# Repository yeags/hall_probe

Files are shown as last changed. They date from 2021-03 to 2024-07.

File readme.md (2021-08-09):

# Hall Probe / CMM Integration
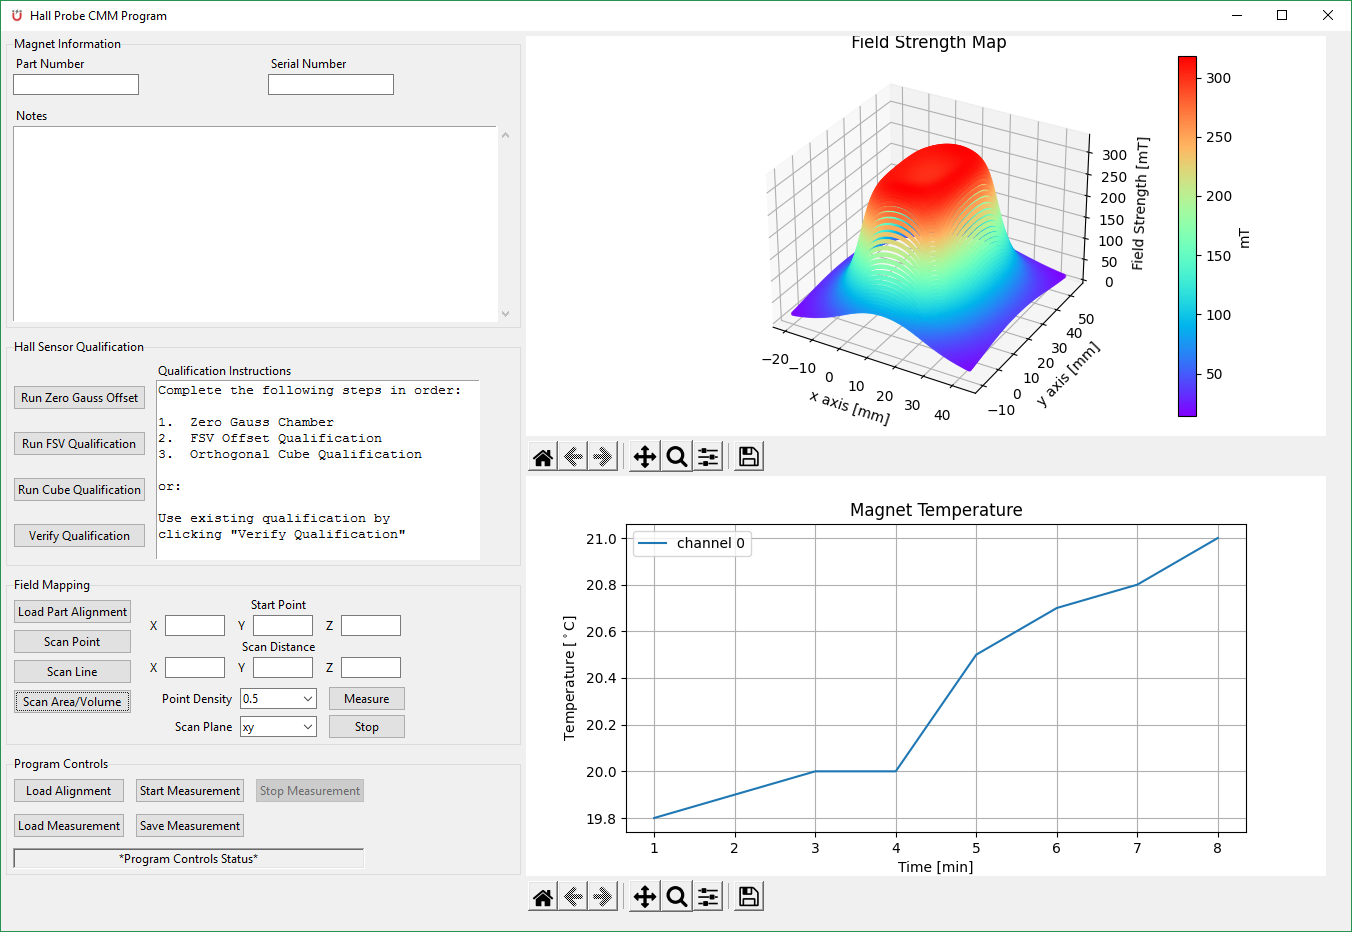
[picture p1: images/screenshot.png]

## Intro

This project is designed to integrate a Senis 3-axis hall sensor with a Zeiss Accura CMM.
Instead of using a start-and-stop method of mapping a magnetic field, this system will map on-the-fly along a given path.  The advantages to this method is a major time savings for large mapping areas while only sacrificing a relatively small amount of positional accuracy.

## Equipment and Hardware
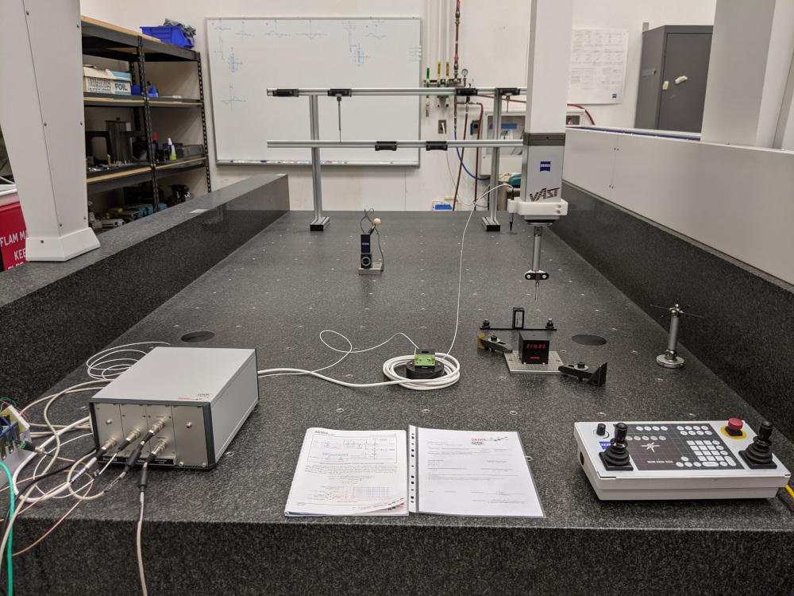
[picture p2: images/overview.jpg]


### **Zeiss Accura CMM**
The CMM used here is a Zeiss Accura model with a VAST Gold measurement sensor.  The controller box is C99.  The commands python sends to the controller are relatively basic compared to its native communication with Calypso, however, it tends to do the job nicely.  
This setup will work with other Zeiss CMMs so long as a C99 controller box is used, which is most likely the case unless it is a very old machine.  The CMM used here is about 15 years old.

### **National Instruments cDAQ**
* cDAQ-9185 CompactDAQ Chassis, 4-slot
* NI-9212 C Series Temperature Input Module
* NI-9229 C Series Voltage Input Module
* NI-9263 C Series Voltage Output Module

The two main modules of the NI cDAQ are the voltage input and output.
The voltage input module is used to read the ± 12 V analog signal and convert it to digital values.  It also reads the on-board temperature sensor of the hall probe.  
The voltage output module sends a 1.3 V signal to turn on the electronic control box and 5 V signals to turn on the current for the FSV tool and select the sensitivity range of the hall sensor.

### **Senis Electronic Control Box**
This electronic control box performs the following tasks:

* Takes in the signals generated from the hall sensor and outputs a ± 12 V analog signal.
* Supplies current to the FSV tool.
* Takes input in the form of 5 V to switch on/off the box itself, current for the FSV tool, and select sensitivity range of the hall sensor.

### **Field Sensitive Volume (FSV) Tool**
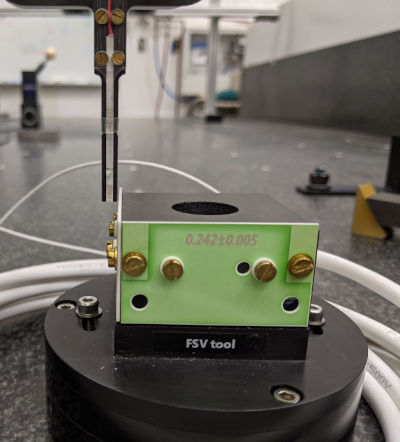
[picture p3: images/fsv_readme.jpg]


The FSV tool is used to determine the x, y, and z spatial offset relative to the master probe.  Since all travel commands sent to the CMM are with respect to the master probe, those coordinates need to take the different position of the hallprobe into consideration.  A Calypso CMM program is used to establish a local coordinate system of the FSV tool.  The FSV tool does not need to be aligned with the machine coordinate system (MCS) for qualification to take place.  A Calypso PCM script is used to generate rotation and translation values between the local part coordinate system (PCS) and the MCS.

### **Orthogonal Cube**
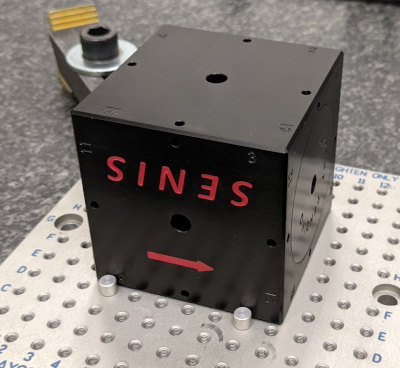
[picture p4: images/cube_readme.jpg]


The orthogonal cube helps correct any non-orthogonality due to sensor placement within the ceramic probe.  This, alongside an additional Calypso program helps establish rotational correction with respect to the MCS.

## Software

The entire project is written in Python.  So far this is still a work in progress and code may break or change in the meantime.  GUI started out as an empty proof of concept and is slowly being modified to contain actual functionality.  Currently only the probe qualification routines are integrated and working within the graphical interface.

### **Prerequisites**

National Instruments NI-DAQmx drivers must be installed.  Software version 20.0 is used here.  Newer versions have not been tested with this system.  
Driver software can be found from NI's website [here](https://www.ni.com/en-us/support/downloads/drivers/download.ni-daqmx.html#346240).  
Device names in the python scripts are static and must be renamed in NI MAX to the following:
* cDAQ-9185 "MagnetcDAQ"
* NI-9212 "MagnetTemp"
* NI-9229 "FieldSensor"
* NI-9263 "AnalogOut"

Third party python libraries utilized are:
* numpy
* matplotlib
* Pillow
* nidaqmx

All libraries are installable via pip.  For example:

>`pip install nidaqmx`

### **Graphical Interface**

The graphical interface was built with python's included library, tkinter.  The main purpose of the GUI is to simplify the magnet measurement process.  The interface is broken down into the following sections:

* Magnet Information
  * Enter in part and serial number information as well as any relevant notes that pertain to the part in question.
* Probe Qualification
  * Contains a step-by-step guide for qualifying a newly setup hall probe.
* Measurement Controls
  * Input parameters to perform magnet measurements
  * Only point and line measurements are complete and functional.  Area mapping is still a work in progress.
* Program Controls
  * Buttons for creating a new measurement plan, saving, or opening an existing one.
  * No functional controls yet.  This section is still a work in progress.
* Visualization Controls
  * Create various plots from the measurement results
  * This section is still a work in progress
* TBD - Alignment Analysis
  * Still TBD, but possibly output data useful for alignment purposes.

### **Zeiss Calypso CMM Software**

The main use of the Calypso CMM software is to physically measure the part in order to determine the relationship between the PCS and MCS so that the hall probe can accurately travel to known points in space in relation to the aligned part system.  PCM (an optional add-on to the standard Calypso package) is used in order to generate a text file containing the transformation matrix needed for hallprobe scanning.  
The PCM script is entered into Calypso's measurement plan post-settings PCM window.  
```
if fileExists("alignment.txt"):
	deleteFile("alignment.txt")
endif
writeDiffCoordSysToFile("MCS", "PCS", "alignment.txt")
```
If PCM is not installed, one can manually execute the `writeDiffCoordSysToFile` function using a Result Element characteristic and executing a formula.

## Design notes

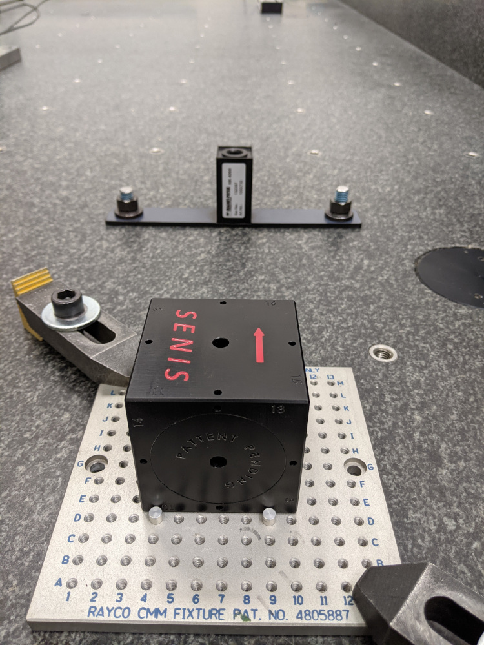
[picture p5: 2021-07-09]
images/cube_y1.jpg

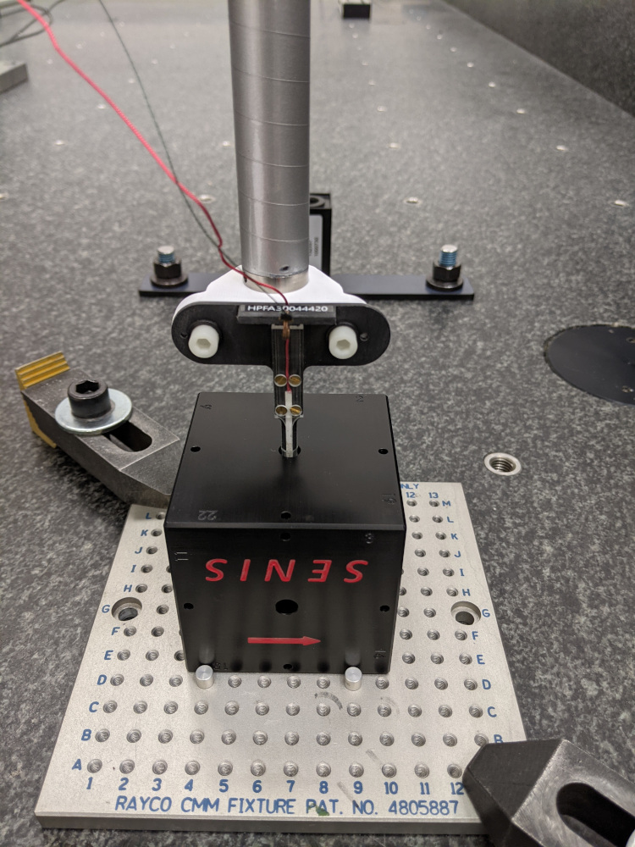
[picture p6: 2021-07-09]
images/cube_x1.jpg

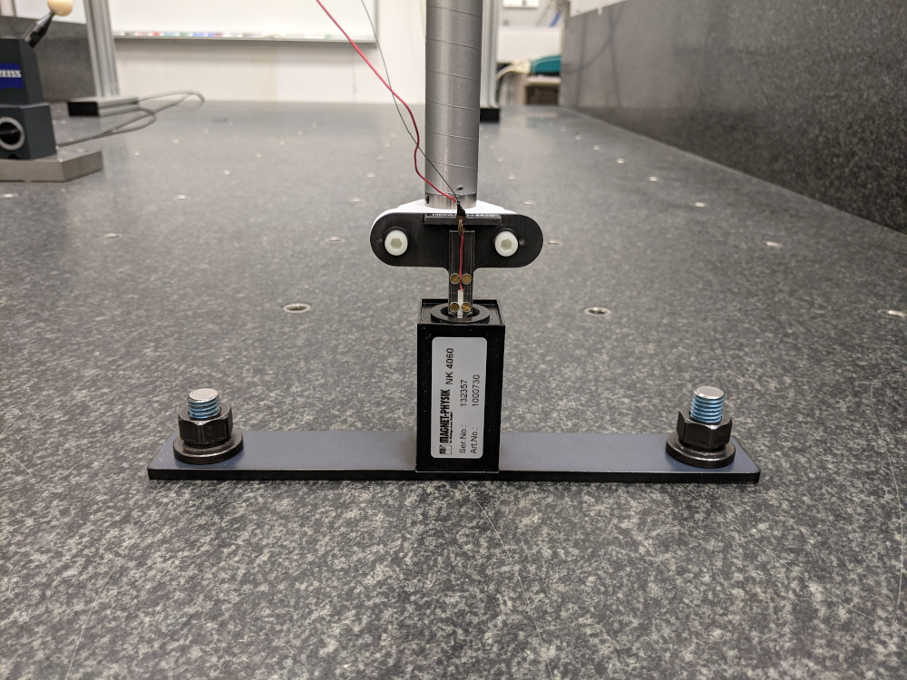
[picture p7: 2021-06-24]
images/zg_chamber1.jpg

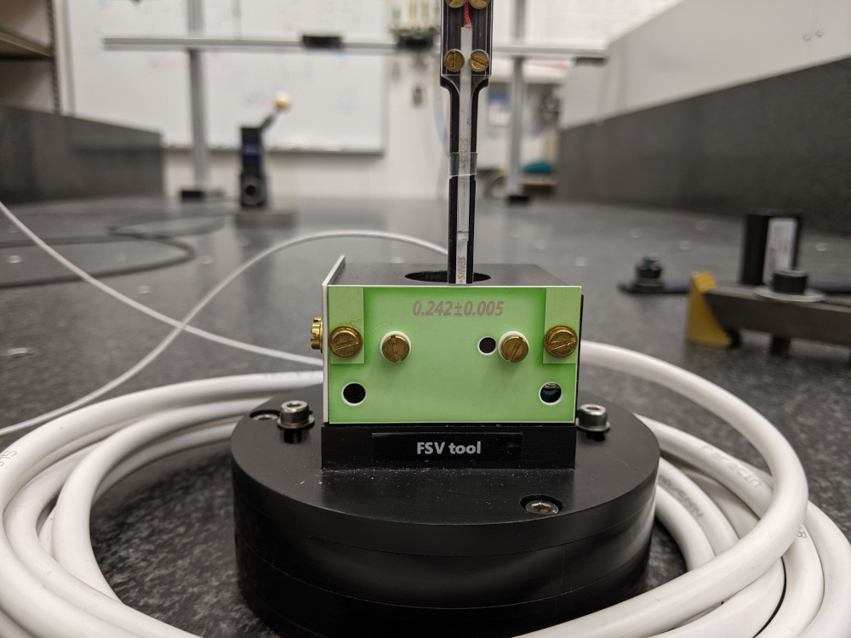
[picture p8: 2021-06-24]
images/fsv_y.jpg

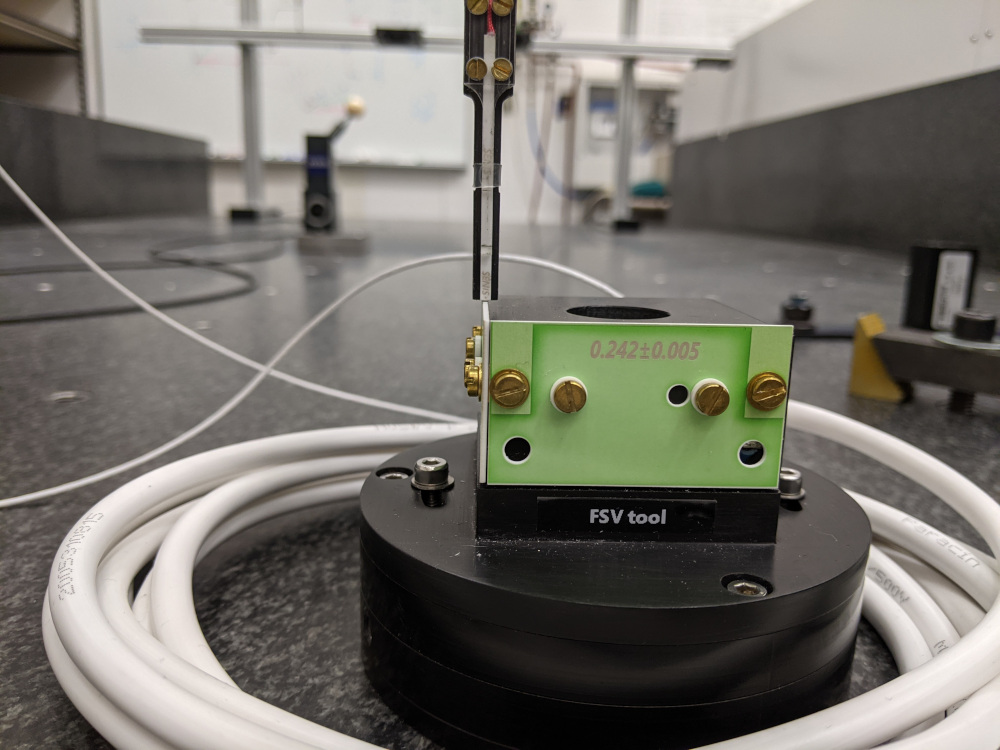
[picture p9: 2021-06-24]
images/fsv_x.jpg

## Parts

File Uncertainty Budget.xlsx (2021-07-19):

Scan speed | 5 | mm/s
Sample rate (approx) | 1578 | S/s
Combined uncertainty | 0.02307234997
k=2 | 0.04614469995
Source | Value | Units | Sensitivity Coefficient | Probability Distribution | Divisor | Standard Uncertainty | Notes
Packet latency | 0.0015 | s | 5 | exponential | 1 | 0.0075 | using geometric mean. (std dev == mean)
CMM position | 0.0035 | mm | 1 | rectangular | 1.732050808 | 0.002020725942
FSV x position error | 0.006 | mm | 1 | normal | 1 | 0.006
FSV y position error | 0.006 | mm | 1 | normal | 1 | 0.006
FSV z position error | 0.020 | mm | 1 | normal | 1 | 0.02

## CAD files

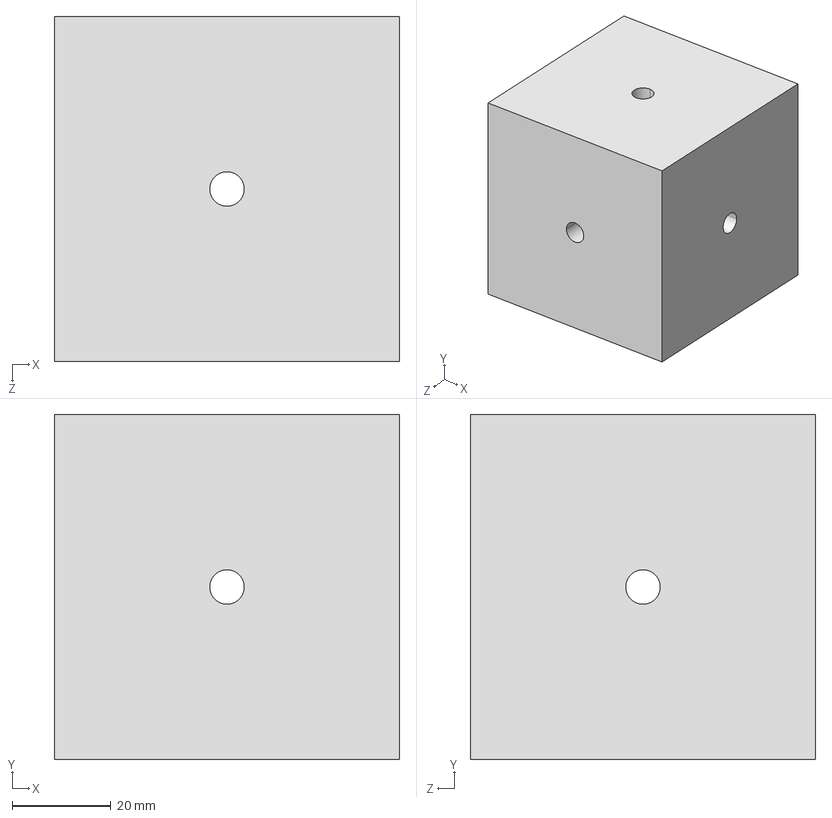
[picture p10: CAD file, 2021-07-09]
cube.STEP
70.0 x 70.0 x 70.0 mm

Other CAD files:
cube.SLDPRT

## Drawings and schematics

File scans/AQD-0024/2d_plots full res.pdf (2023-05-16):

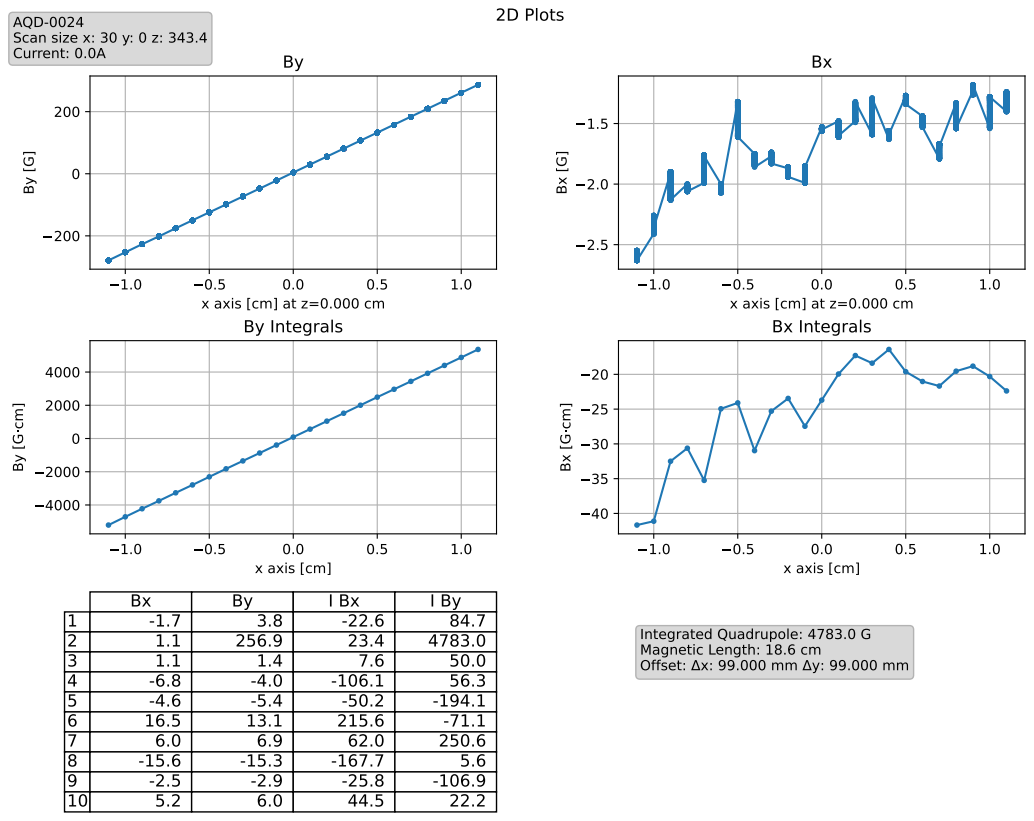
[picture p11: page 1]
x axis [cm]; 2D Plots AQD-0024; Scan size x: 30 y: 0 z: 343.4 Current: 0.0A

x axis [cm] at z=0.000 cm
By Integrals

Bx Integrals

Integrated Quadrupole: 4783.0 G
Magnetic Length: 18.6 cm
Offset: x: 99.000 mm y: 99.000 mm

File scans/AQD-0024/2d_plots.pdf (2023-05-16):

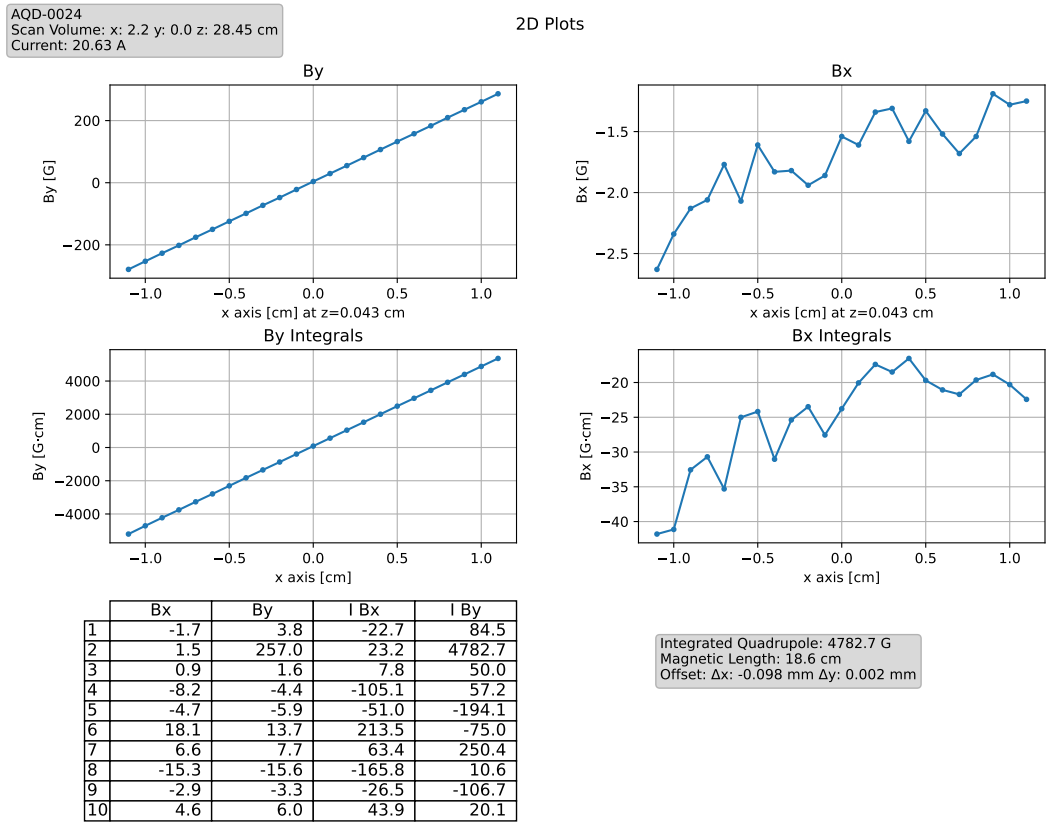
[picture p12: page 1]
x axis [cm]

2D Plots AQD-0024
Scan Volume: x: 2.2 y: 0.0 z: 28.45 cm
Current: 20.63 A

x axis [cm] at z=0.043 cm
By Integrals

Bx Integrals

Integrated Quadrupole: 4782.7 G
Magnetic Length: 18.6 cm
Offset: x: -0.098 mm y: 0.002 mm

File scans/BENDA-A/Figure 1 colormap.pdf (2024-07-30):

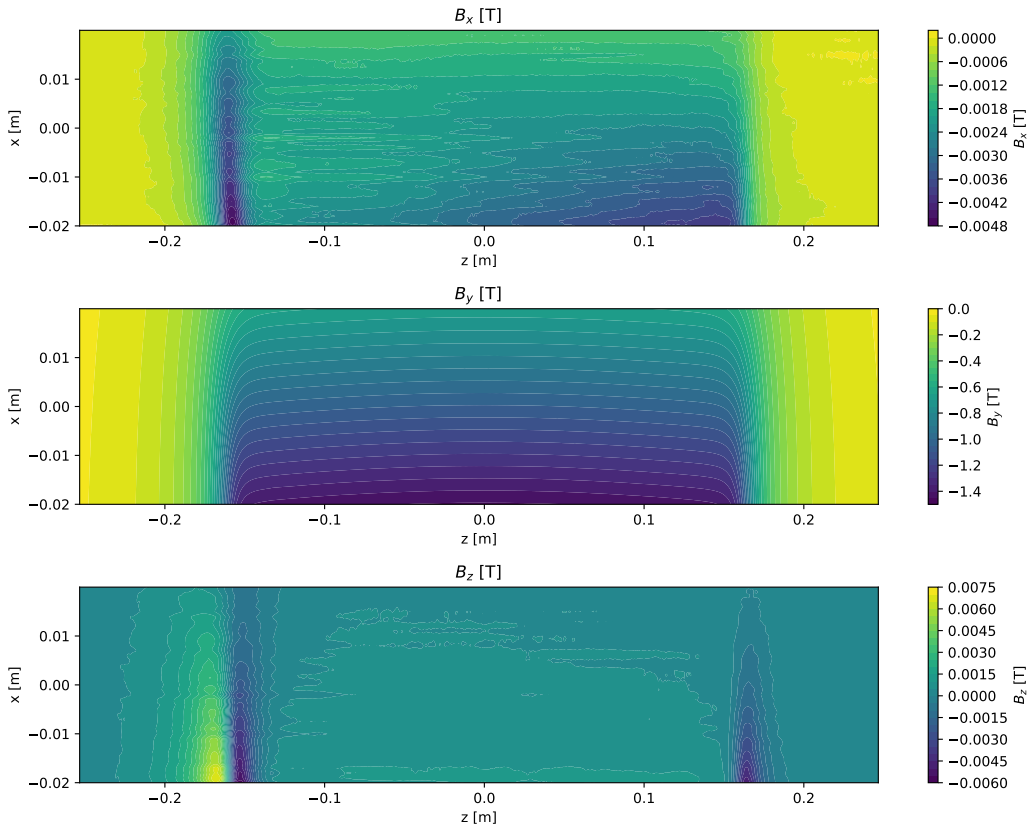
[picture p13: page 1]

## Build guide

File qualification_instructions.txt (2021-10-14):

Complete the following steps in order:

1.  Zero Gauss Chamber
2.  FSV Offset Qualification
3.  Orthogonal Cube Qualification

or:

Use existing qualification by
clicking "Verify Qualification"

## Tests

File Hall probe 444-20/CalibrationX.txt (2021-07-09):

-0.0980000	0.0000211	0.0041000	-0.0013300	0.7040000	0.3900000	57.0000000	100 mT
0.0000000	0.0000000	0.0000000	0.0000000	1.0000000	0.0000000	1.0000000	500 mT
-0.0670000	0.0001931	0.0033388	-0.0005200	0.9885830	0.3900000	57.0000000	2 T
********************************************************************************************************************							
System serial number: S/N:							
Probe type and serial number: F3A-03HM05D-S.1T-02T-2K5J S/N: HPFA30044420							
Calibration date: 9/4/2020 							
FSV to edge distance: X= 0.48 mm Y= 1 mm Z= 0.3 mm							
Probe dimension: X= 0.77 mm Y= 2.01 mm							
********************************************************************************************************************

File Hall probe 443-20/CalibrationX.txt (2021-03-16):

0.2160000	0.0000277	0.0047000	0.0036900	0.6750000	0.3400000	57.0000000	100 mT
0.0000000	0.0000000	0.0000000	0.0000000	1.0000000	0.0000000	1.0000000	500 mT
0.0510000	0.0002175	0.0039586	0.0000000	0.9430000	0.3400000	57.0000000	2 T
********************************************************************************************************************							
System serial number: S/N:							
Probe type and serial number: F3A-03HM05D-S.1T-02T-2K5J S/N: HPFA30044320							
Calibration date: 9/3/2020 							
FSV to edge distance: X= 0.49 mm Y= 0.99 mm Z= 0.3 mm							
Probe dimension: X= 0.77 mm Y= 2.01 mm							
********************************************************************************************************************

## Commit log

2020-09-08 added frames
2020-09-08 added voltage channel boxes
2020-09-09 added graph frame
2020-09-11 added to voltage controls
2020-09-18 changed frame organisation
2020-09-25 updated parent frame reference and added to daq
2020-09-25 added sampling frame
2020-10-01 added missing parent frame objects
2020-12-03 minor updates
    [Uncertainty Budget.xlsx]
2021-04-08 added filter function
2021-04-20 updated filter_data func
2021-05-27 moved to obsolete
    [packet_time.csv, packet_time.xlsx]
2021-06-02 switched current direction
2021-07-09 removed unnecessary files
    [cube.SLDPRT, cube.STEP, packet_time.csv, packet_time.xlsx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]
2021-07-19 minor update
    [Uncertainty Budget.xlsx]
2022-11-30 fixed point meas, added filtering
2023-05-16 current plots
2025-01-06 uploading current changes
